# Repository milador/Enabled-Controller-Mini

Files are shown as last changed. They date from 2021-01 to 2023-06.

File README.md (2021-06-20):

# Enabled-Controller-Mini

Enabled Controller Mini is a more affordable version of <a href="https://github.com/milador/Enabled-Controller">Enabled-Controller</a> which is an open-source switch controller interface that enables those with limited or no hand movement to use Adaptive switches as input to operate and perform joystick actions.

<p align="center">
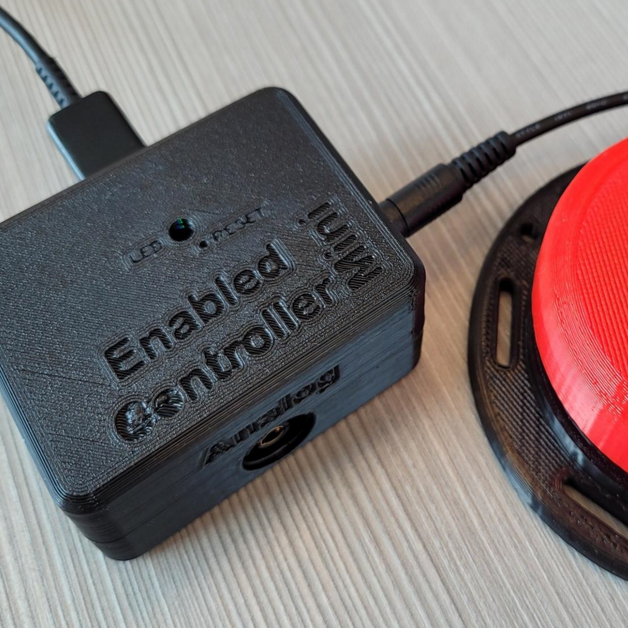
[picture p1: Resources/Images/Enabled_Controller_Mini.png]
Enabled Controller Mini

</p>

The device offers up to four switch input enclosures through four 3.5mm audio jacks and two analog inputs through one 3.5mm headphone jack. The one 3.5mm headphone jacks can be used to connect one X-Y analog joystick.

The internal RGB led of QT Py board is used to provide visual feedback for each action.

## Assembly Instructions Manual

The <a href="https://github.com/milador/Enabled-Controller-Mini/blob/main/Documentation/Build_Manuals/Enabled_Controller_Mini_Instructions_Manual.pdf">Assembly Instructions Manual</a> is available to download.

## Parts

The <a href="https://github.com/milador/Enabled-Controller-Mini/blob/main/Components/Enabled_Controller_Mini_BOM.csv">BOM</a> file is available to download.

## Software

The first experimental software is under testing.

## Hardware 

### PCB Design 

The <a href="https://github.com/milador/Enabled-Controller-Mini/tree/main/Hardware/PCB">PCB files</a> including both PCB Eagle design files and generated gerber files are available to download.

### Enclosure

The <a href="https://github.com/milador/Enabled-Controller-Mini/tree/main/Hardware/Enclosure">Enclosure files</a> including both STL and STEP enclosure files are available to download.

## License

### Creative Commons Attribution-NonCommercial-ShareAlike (CC-BY-NC-SA)

Copyright (c) 2021 Milador

A creative commons license that bans commercial use and requires you to release any modified works under this license.

<p align="center">
CC-BY-NC-SA
</p>

<br />This work is licensed under a <a rel="license" href="http://creativecommons.org/licenses/by-nc-sa/3.0/">Creative Commons Attribution-NonCommercial-ShareAlike 3.0 Unported License</a>.

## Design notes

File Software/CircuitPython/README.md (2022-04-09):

# Enabled-Controller-Mini CircuitPython software setup

  1. Download the latest version of [CircuitPython for QT Py UF2](https://circuitpython.org/board/qtpy_m0/) from official website or the latest [Tested CircuitPython for QT Py UF2](https://github.com/milador/Enabled-Controller-Mini/raw/main/Software/CircuitPython/UF2/adafruit-circuitpython-qtpy_m0-en_US-6.0.1.uf2) from this repository.
  2. Plug your QT Py into your computer using a known-good USB cable
  3. Double-click the small RST (reset) button, and you will see the NeoPixel RGB LED turn green
  4. You will see a new disk drive appear called QTPY_BOOT under Device and Drivers 
  5. Drag the adafruit_circuitpython_etc.uf2 file to QTPY_BOOT
  6. The red LED will flash. Then, the QTPY_BOOT drive will disappear and a new disk drive called CIRCUITPY will appear
  7. Replace the code.py under CIRCUITPY drive with Enabled-Controller-Mini USB [code.py](https://raw.githubusercontent.com/milador/Enabled-Controller-Mini/main/Software/CircuitPython/Enabled_Controller_Mini_USB_Software/code.py)
  8. Drag and drop required libraries under CIRCUITPY drive in lib folder. [Required libraries](https://github.com/milador/Enabled-Controller-Mini/tree/main/Software/CircuitPython/Enabled_Controller_Mini_USB_Software/lib)
  9. The led on Enabled-Controller-Mini should turn to teal color

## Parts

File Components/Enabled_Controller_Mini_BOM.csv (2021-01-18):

Index | Quantity | Digikey Part Number | Manufacturer Part Number | Description | Price (CAD) | Unit Price (CAD) | Link
1 | 1 | 1528-4600-ND | 4600 | ADAFRUIT QT PY - SAMD21 DEV BOARD | 8.31 | 8.31 | https://www.digikey.ca/en/products/detail/adafruit-industries-llc/4600/13543375
2 | 2 | S7040-ND | PPPC071LFBN-RC | CONN HDR 7POS 0.1 GOLD | 0.84 | 0.84 | https://www.digikey.ca/en/products/detail/sullins-connector-solutions/PPPC071LFBN-RC/810179
3 | 4 | CP1-3535NG-ND | SJ1-3535NG | CONN JACK STEREO 3.5MM R/A | 1.65 | 1.65 | https://www.digikey.ca/product-detail/en/cui-inc/SJ1-3535NG/CP1-3535NG-ND
4 | 1 | CP-43514-ND | SJ-43514 | CONN JACK 4COND 3.5MM | 1.47 | 1.47 | https://www.digikey.ca/en/products/detail/SJ-43514/CP-43514-ND/368146
5 | 4 | 36-4701-ND | 4701 | HEX NUT 0.245" STEEL 6-32 | 0.15 | 0.15 | https://www.digikey.ca/en/products/detail/keystone-electronics/4701/316272
6 | 4 | 36-9309-ND | 9309 | MACH SCREW PAN HEAD SLOTTED 6-32 | 0.15 | 0.15 | https://www.digikey.ca/en/products/detail/keystone-electronics/9309/2746088
 |  |  |  |  | Total Price (CAD) | 19.26

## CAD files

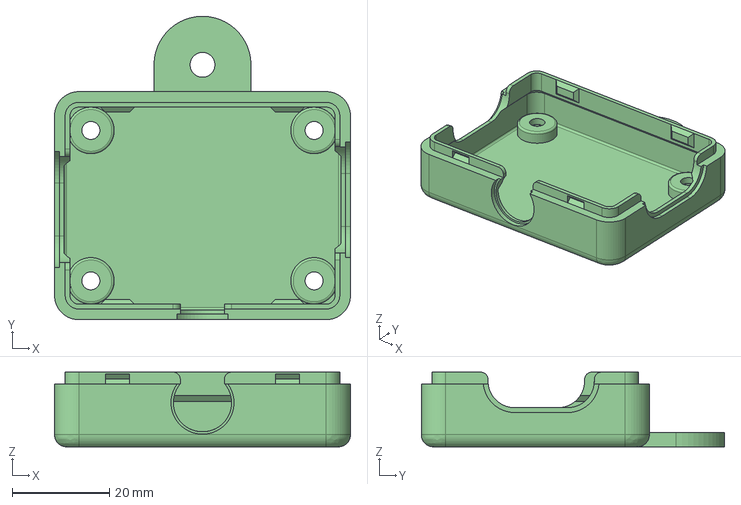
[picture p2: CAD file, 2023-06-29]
Hardware/Enclosure/STEP/Enabled_Controller_Mini_Bottom_With_Mount.step
61.0 x 62.5 x 15.4 mm

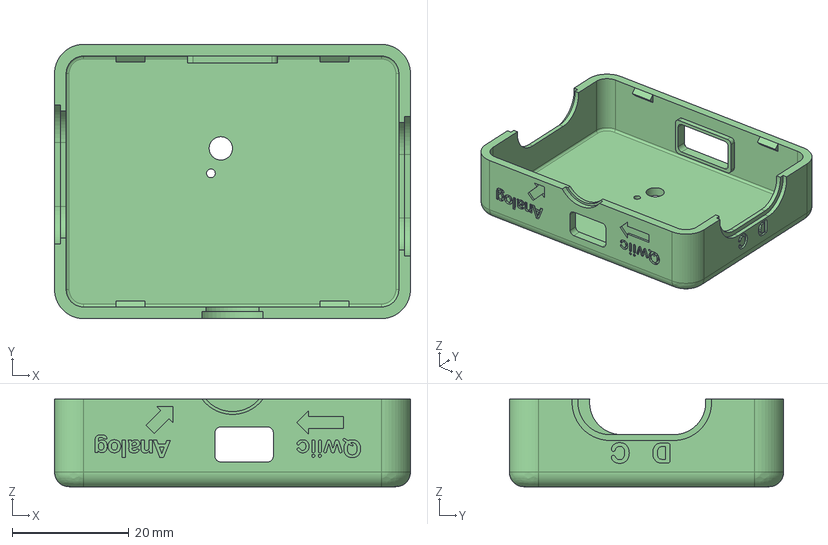
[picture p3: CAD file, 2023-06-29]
Hardware/Enclosure/STEP/Enabled_Controller_Mini_Top.step
61.0 x 47.0 x 15.0 mm

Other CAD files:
Hardware/Enclosure/STEP/Enabled_Controller_Mini_Bottom.step
Hardware/Enclosure/STL/Enabled_Controller_Mini_Bottom.stl
Hardware/Enclosure/STL/Enabled_Controller_Mini_Bottom_With_Mount.stl
Hardware/Enclosure/STL/Enabled_Controller_Mini_Top.stl

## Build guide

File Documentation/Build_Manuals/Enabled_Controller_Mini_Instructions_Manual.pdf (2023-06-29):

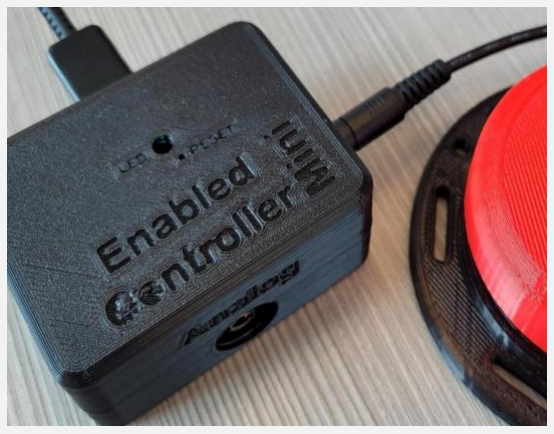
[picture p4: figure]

# ENABLED-CONTROLLER-MINI INSTRUCTIONS MANUAL (V1.3)

An accessible switch adapter box for gaming

### Milad Hajihassan

https://github.com/milador/Enabled-Controller-Mini

1

## Contents

Components List | 2
Software | 3
Installing Arduino IDE | 3
Installing Arduino Libraries | 3
USB Version | 3
Board Support Packages | 3
Required Software and libraries | 4
Uploading Software | 5
Joystick Version | 6
Board Support Packages | 6
Required Software and libraries | 6
Uploading Software | 7
Hardware Assembly | 8
Printed circuit Board design | 8
Enclosure design | 8
Enabled-Controller-Mini Assembly | 9
Joystick Assembly | 21

2

## Components List

1. ADAFRUIT QT PY - SAMD21 DEV BOARD x 1
2. 7 POSITION HEADER x 2
3. CONN JACK STEREO 3.5MM R/A x 4
4. CONN JACK 4COND 3.5MM x 1
5. ANALOG 2-AXIS THUMB JOYSTICK WIT (Optional) x 1
6. HEX NUT 0.245" STEEL 6-32 x 4
7. MACH SCREW PAN HEAD SLOTTED 6-32 x 4

The bill of materials can also be downloaded from GitHub repository under main directory.

https://github.com/milador/Enabled-Controller-

Mini/blob/master/Components/Enabled_Controller_Mini_BOM.csv (https://github.com/milador/Enabled-Controller-Mini/blob/master/Components/Enabled_Controller_Mini_BOM.csv)

3

## Software

The Enabled-Controller-Mini software can be downloaded from the GitHub repository under software directory.

https://github.com/milador/Enabled-Controller-Mini/tree/master/Software/Arduino/

There are two flavors of Enabled-Controller-Mini and each one requires different hardware. The Enabled-Controller-Mini software is offered in the following flavors:

1. USB Keyboard/Mouse Version
2. Joystick Version

### Installing Arduino IDE

The Arduino IDE is required to compile and upload the source code to the MCU in your Adafruit QT Py board. You can download and install the Arduino from official Arduino website that you can find using following link:

https://www.arduino.cc/en/software

### Installing Arduino Libraries

The following instructions on how to install additional Arduino libraries helps you to get started with setting up Arduino IDE with required libraries and dependencies.

https://www.arduino.cc/en/guide/libraries

### USB Version

Board Support Packages
You can find the official instructions to install Board Support Packages on Adafruit website using following link:

https://learn.adafruit.com/adafruit-qt-py/arduino-ide-setup

Alternatively, you can perform following instructions to install Board Support Packages:

1. Open and start the Arduino IDE.
2. Go to File > Preferences.
3. Add following link as a new line under Additional Board Manager URLs
- https://adafruit.github.io/arduino-board-index/package_adafruit_index.json
4. Restart the Arduino IDE
5. Open the Boards Manager option from the Tools > Board menu and install Adafruit SAMD Boards by Adafruit
6. Wait until the IDE finishes installing the cross-compiling toolchain and tools associated with Board Support Package. This may take few minutes.
7. That’s it! The installation of Board Support Packages is finished.

4

Required Software and libraries
The USB version of the software requires the following files and libraries:
- StopWatch library (https://github.com/RobTillaart/Stopwatch_RT)
- EasyMorse library (https://github.com/milador/EasyMorse)
- Adafruit_NeoPixel library (https://github.com/adafruit/Adafruit_NeoPixel)
- FlashStorage library (https://github.com/cmaglie/FlashStorage)
- Enabled_Controller_Mini_USB_Software.ino (https://raw.githubusercontent.com/milador/Enabled-Controller-Mini/main/Software/Arduino/Enabled_Controller_Mini_USB_Software/Enabled_Controller_Mini_USB_Softw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)

StopWatch library helps to calculate the reaction time and timeout in the morse code interface.

Enabled-Controller-Mini is using Adafruit_NeoPixel library to provide visual feedback using RGB LED.

You can use the following instructions to download and install the required libraries:

1) Visit the StopWatch library (https://github.com/RobTillaart/Stopwatch_RT) github repository page.
2) Click on Code > Download Zip to download StopWatch library.
3) Extract Stopwatch_RT-master.zip file
4) Rename Stopwatch_RT-master folder to Stopwatch folder under Stopwatch_RT-master subdirectory.
5) Copy or move Stopwatch folder to Arduino installation library subdirectory. As an example: This is found under C:\Program Files (x86)\Arduino\libraries in windows 10.
6) Visit the EasyMorse library (https://github.com/milador/EasyMorse) github repository page.
7) Click on Code > Download Zip to download EasyMorse library.
8) Extract EasyMorse-master.zip file
9) Rename EasyMorse-master folder to EasyMorse folder under EasyMorse-master subdirectory.
10) Copy or move EasyMorse folder to Arduino installation library subdirectory. As an example: This is found under C:\Program Files (x86)\Arduino\libraries in windows 10.
11) Visit the FlashStorage library (https://github.com/cmaglie/FlashStorage) github repository page.
12) Click on Code > Download Zip to download FlashStorage library.
13) Extract FlashStorage-master.zip file
14) Rename FlashStorage-master folder to FlashStorage folder under FlashStorage-master subdirectory.
15) Copy or move FlashStorage folder to Arduino installation library subdirectory. As an example: This is found under C:\Program Files (x86)\Arduino\libraries in windows 10.
16) Visit the Enabled_Controller_Mini_USB_Software.ino (https://raw.githubusercontent.com/milador/Enabled-Controller-Mini/main/Software/Arduino/Enabled_Controller_Mini_USB_Software/Enabled_Controller_Mini_USB_Softw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) raw source code file under Enabled-Controller-Mini github repository page.
17) Right click on the source code or any place on this page and select Save Page As…
18) Select the directory you would like to save the software in your computer.
19) Change File name from Enabled_Controller_Mini_USB_Software to Enabled_Controller_Mini_USB_Software.ino
20) Change Save as type to All Files.
21) Click on Save button.
22) Open the directory you selected in step 18.
23) Double left click or open Enabled_Controller_Mini_USB_Software file

5

24) Arduino IDE will ask your permission to create a new sketch folder named Enabled_Controller_Mini_USB_Software and move Enabled_Controller_Mini_USB_Software.ino under this folder.
25) Click on the Ok button.
26) Arduino IDE should now open the Enabled_Controller_Mini_USB_Software.ino file automatically.

Uploading Software
Note: Make sure all files are included in your local copy of Software directory before uploading it to the Adafruit QT PY board. The libraries can be installed in Arduino libraries.

You can go ahead and upload the downloaded .ino code to Adafruit QT PY board using Arduino IDE once all the necessary libraries are installed.

1. Start the Arduino IDE
2. Open Enabled_Controller_Mini_USB_Software.ino
3. Select the Board under Tools > Board > Adafruit SAMD Boards as Adafruit QT PY (SAMD21)
4. Select the correct port number under Tools > Port which should show COM XX (Adafruit QT PY)

Note: It’s very important to make sure the correct Board and port number are selected as selecting the wrong board may result problems with bootloader of Adafruit QT PY board.

5. Press the Verify button to make sure there is no problem with the software and libraries.
6. Press Upload button

You can now go ahead and upload the software. Arduino IDE will show you a Done Uploading message indicating the software is uploaded to your Enabled-Controller-Mini.

The LED on the QT PY board blinks two times in teal to indicate the start of initialization process has been started and it will blink again two times in green to indicate end of the initialization process.

You can also open the Serial Monitor in Arduino IDE on 115200 baud-rate to read initialization information about the version of software.

6

### Joystick Version

Board Support Packages
You can find the official instructions to install Board Support Packages on Adafruit website using following link:

https://learn.adafruit.com/adafruit-qt-py/arduino-ide-setup

Alternatively, you can perform following instructions to install Board Support Packages:

1. Open and start the Arduino IDE.
2. Go to File > Preferences.
3. Add following link as a new line under Additional Board Manager URLs
- https://adafruit.github.io/arduino-board-index/package_adafruit_index.json
4. Restart the Arduino IDE
5. Open the Boards Manager option from the Tools > Board menu and install Adafruit SAMD Boards by Adafruit
6. Wait until the IDE finishes installing the cross-compiling toolchain and tools associated with Board Support Package. This may take few minutes.
7. That’s it! The installation of Board Support Packages is finished.

Required Software and libraries
The Joystick version of the software requires the following files and libraries:
- XACGamepad.h header file (https://github.com/milador/Enabled-Controller-Mini/tree/main/Software/Arduino/Enabled_Controller_Mini_Joystick_Software/XACGamepad.h)
- Adafruit_NeoPixel library (https://github.com/adafruit/Adafruit_NeoPixel)
- Enabled_Controller_Mini_Joystick_Software.ino (https://raw.githubusercontent.com/milador/Enabled-Controller-Mini/main/Software/Arduino/Enabled_Controller_Mini_Joystick_Software/Enabled_Controller_Mini_Joys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)

The XACGamepad.h header file (https://github.com/milador/Enabled-Controller-Mini/tree/main/Software/Arduino/Enabled_Controller_Mini_Joystick_Software/XACGamepad.h) is used to turn Enabled Controller Mini into a XAC Compatible joystick USB HID device which can be used for gaming. It uses TinyUSB USB stack instead of Arduino USB stack to create custom Gamepad USB descriptor.

Enabled-Controller-Mini is using Adafruit_NeoPixel library to provide visual feedback using RGB LED.

You can use the following instructions to download and install the required libraries:

1) Visit the Enabled_Controller_Joystick_Software.ino (https://raw.githubusercontent.com/milador/Enabled-Controller-Mini/main/Software/Arduino/Enabled_Controller_Mini_Joystick_Software/Enabled_Controller_Mini_Joys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) raw source code file under Enabled-Controller-Mini github repository page.
2) Right click on the source code or any place on this page and select Save Page As…
3) Select the directory you would like to save the software in your computer.
4) Change File name from Enabled_Controller_Mini_Joystick_Software to Enabled_Controller_Mini_Joystick_Software.ino
5) Change Save as type to All Files.
6) Click on Save button.
7) Visit the XACGamepad.h header file (https://github.com/milador/Enabled-Controller-Mini/tree/main/Software/Arduino/Enabled_Controller_Mini_Joystick_Software/XACGamepad.h) raw source code file under Enabled-Controller-Mini github repository page.
8) Right click on the source code or any place on this page and select Save Page As…

7

9) Select the same directory that you previously saved Enabled_Controller_Mini_Joystick_Software.ino in step 4.
10) Change File name from XACGamepad to XACGamepad.h
11) Change Save as type to All Files.
12) Click on the Save button.
13) Open the directory you selected in step 4.
14) Double left click or open Enabled_Controller_Mini_Joystick_Software file
15) Arduino IDE will ask your permission to create a new sketch folder named Enabled_Controller_Mini_Joystick_Software and move Enabled_Controller_Mini_Joystick_Software.ino under this folder.
16) Click on the Ok button.
17) Arduino IDE should now open the Enabled_Controller_Mini_Joystick_Software.ino file automatically.

Uploading Software
Note: Make sure all files are included in your local copy of Software directory before uploading it to the Adafruit QT PY board. The libraries can be installed in Arduino libraries.

You can go ahead and upload the downloaded .ino code to Adafruit QT Py board using Arduino IDE once all the necessary libraries are installed.

1. Start the Arduino IDE
2. Open Enabled_Controller_Mini_Joystick _Software.ino
3. Select the Board under Tools > Board > Adafruit SAMD Boards as Adafruit QT PY (SAMD21)
4. Select the USB Stack Tools > USB Stack as TinyUSB
5. Select the correct port number under Tools > Port which should show COM XX (Adafruit QT PY)

Note: It’s very important to make sure the correct Board and port number are selected as selecting the wrong board may result problems with bootloader of Adafruit QT PY board.

6. Press the Verify button to make sure there is no problem with the software and libraries.
7. Press Upload button

You can now go ahead and upload the software. Arduino IDE will show you a Done Uploading message indicating the software is uploaded to your Enabled-Controller-Mini.

The LED on the QT PY board blinks two times in teal to indicate the start of initialization process has been started and it will blink again two times in green to indicate end of the initialization process.

You can also open the Serial Monitor in Arduino IDE on 115200 baud-rate to read initialization information about the version of software.

8

## Hardware Assembly

### Printed circuit Board design

The printed circuit boards (PCB) can be downloaded from GitHub repository under Hardware directory.

https://github.com/milador/Enabled-Controller-Mini/tree/master/Hardware/PCB

### Enclosure design

The enclosure/housing files in STL format can be downloaded from GitHub repository under Hardware directory.

https://github.com/milador/Enabled-Controller-Mini/tree/master/Hardware/Enclosure

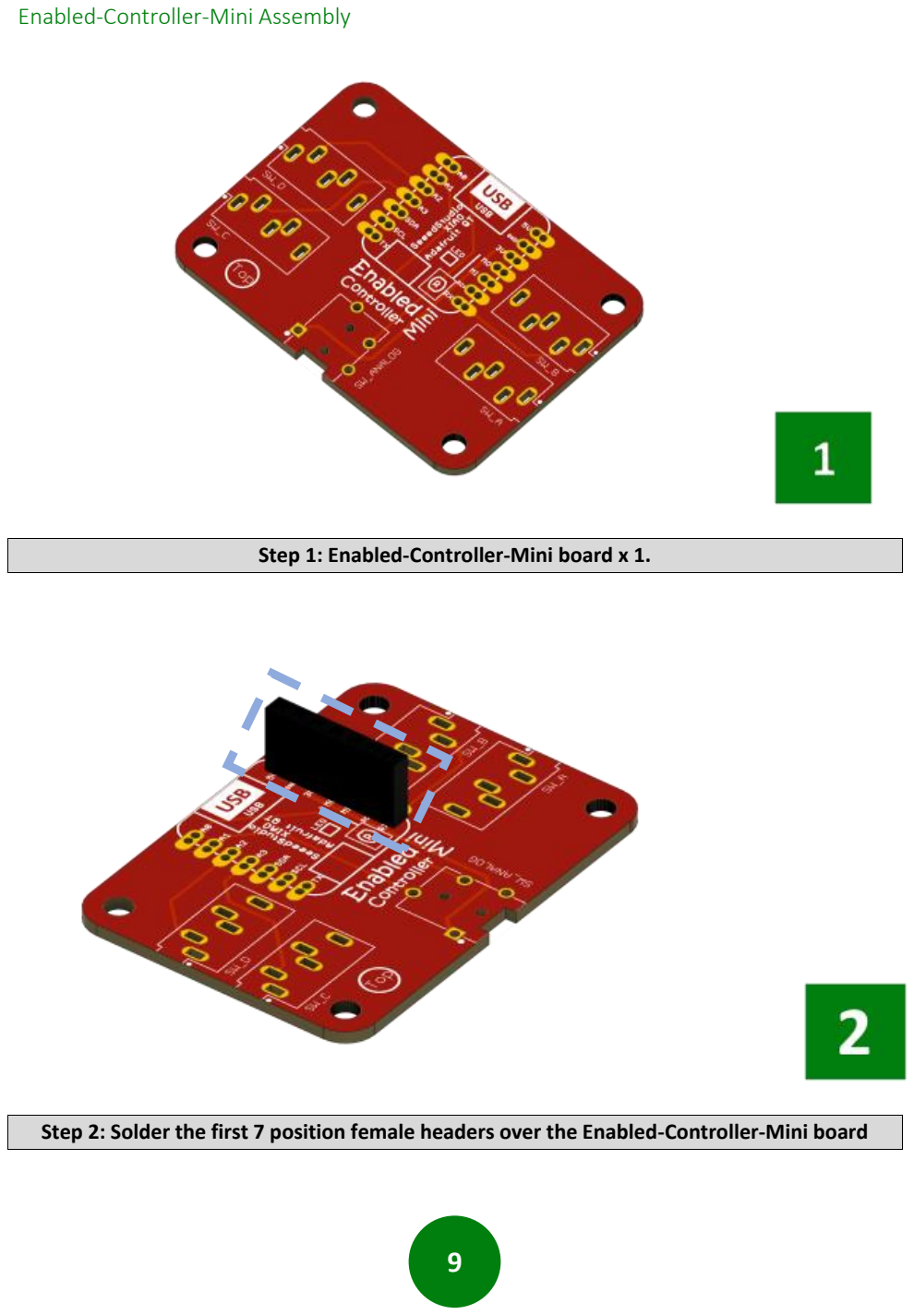
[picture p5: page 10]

9

### Enabled-Controller-Mini Assembly

Step 1: Enabled-Controller-Mini board x 1.
Step 2: Solder the first 7 position female headers over the Enabled-Controller-Mini board

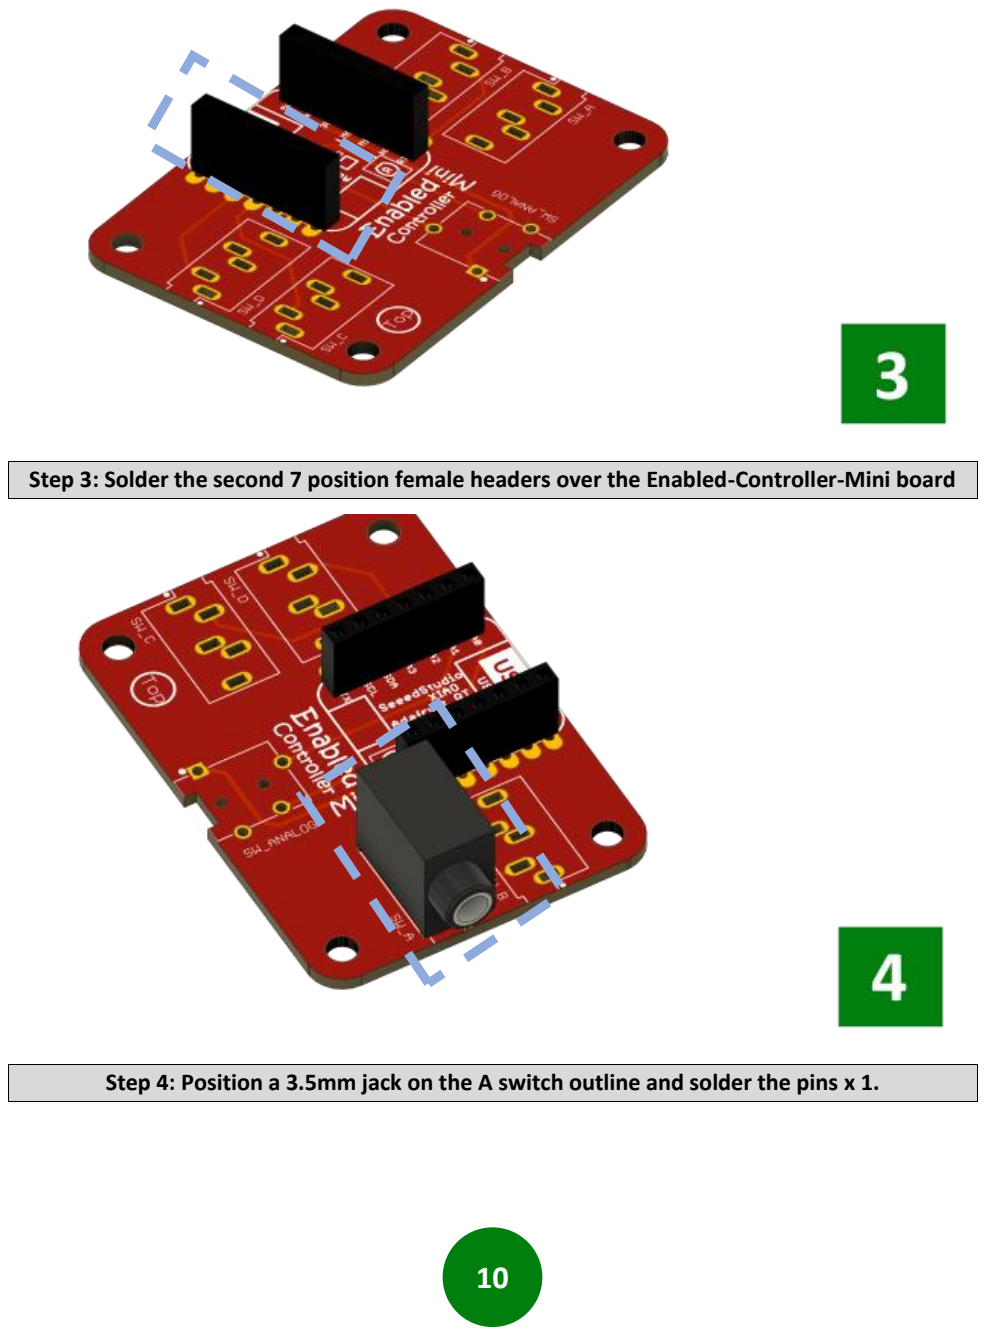
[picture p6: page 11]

10

Step 3: Solder the second 7 position female headers over the Enabled-Controller-Mini board
Step 4: Position a 3.5mm jack on the A switch outline and solder the pins x 1.

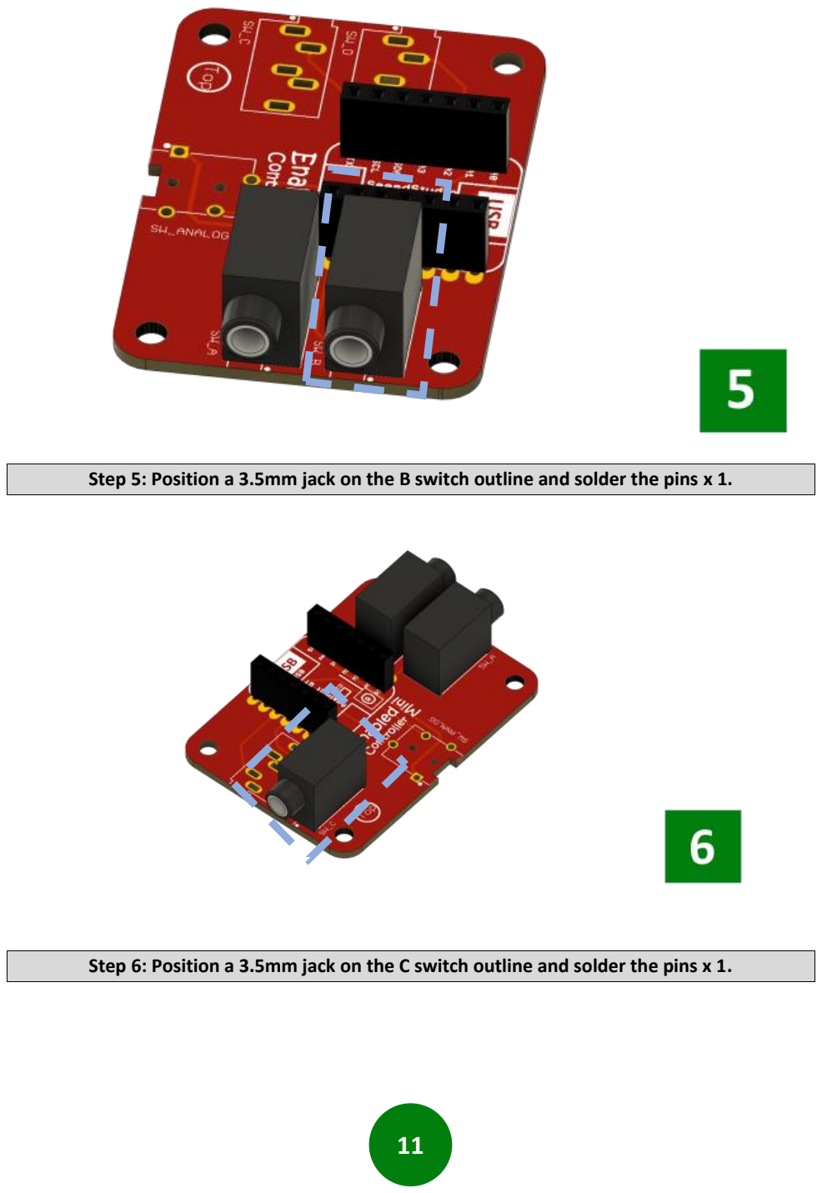
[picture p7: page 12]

11

Step 5: Position a 3.5mm jack on the B switch outline and solder the pins x 1.
Step 6: Position a 3.5mm jack on the C switch outline and solder the pins x 1.

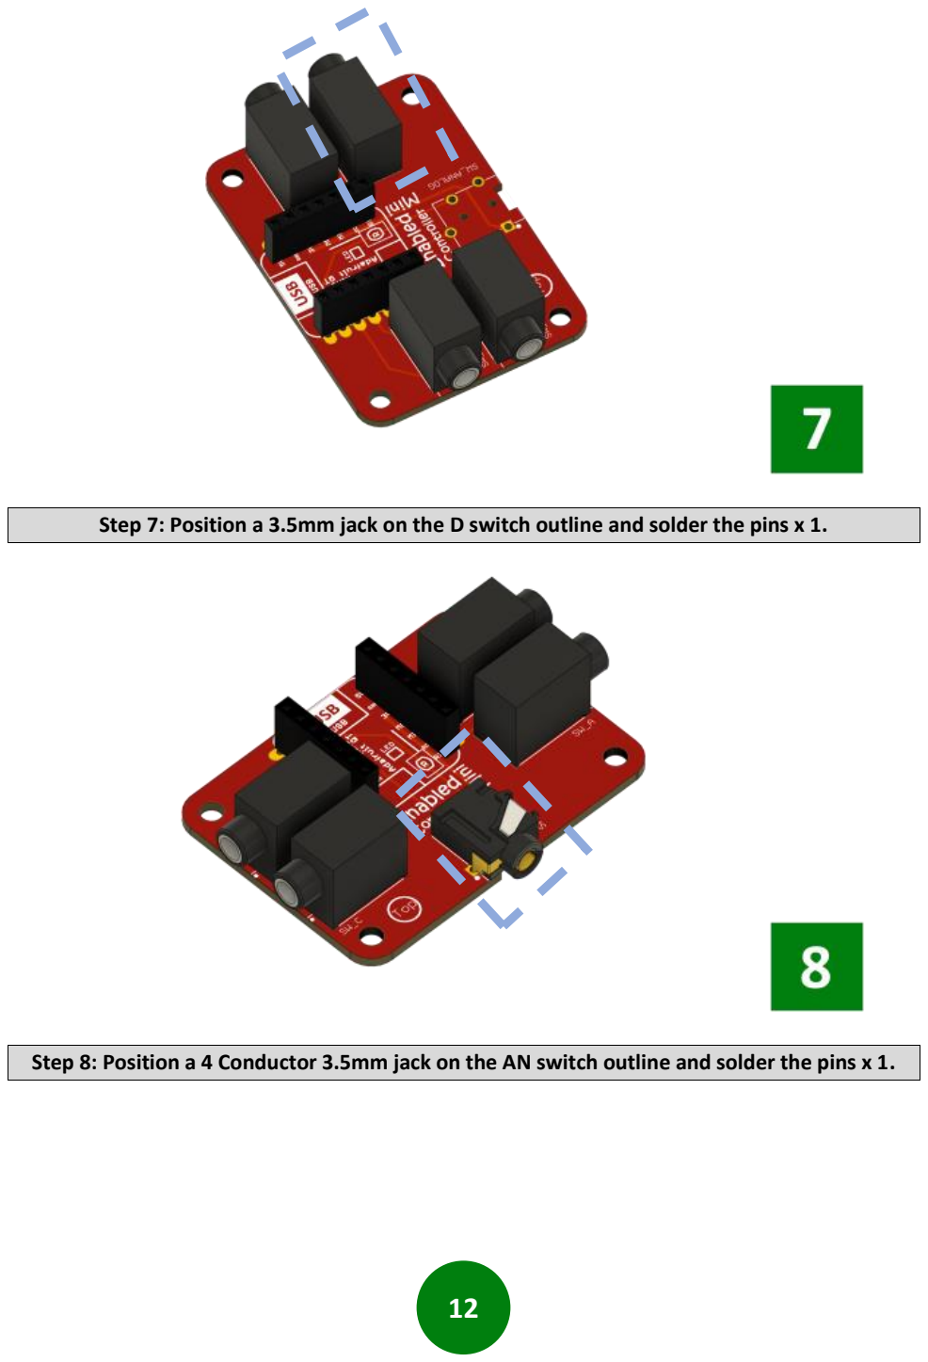
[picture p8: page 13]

12

Step 7: Position a 3.5mm jack on the D switch outline and solder the pins x 1.
Step 8: Position a 4 Conductor 3.5mm jack on the AN switch outline and solder the pins x 1.

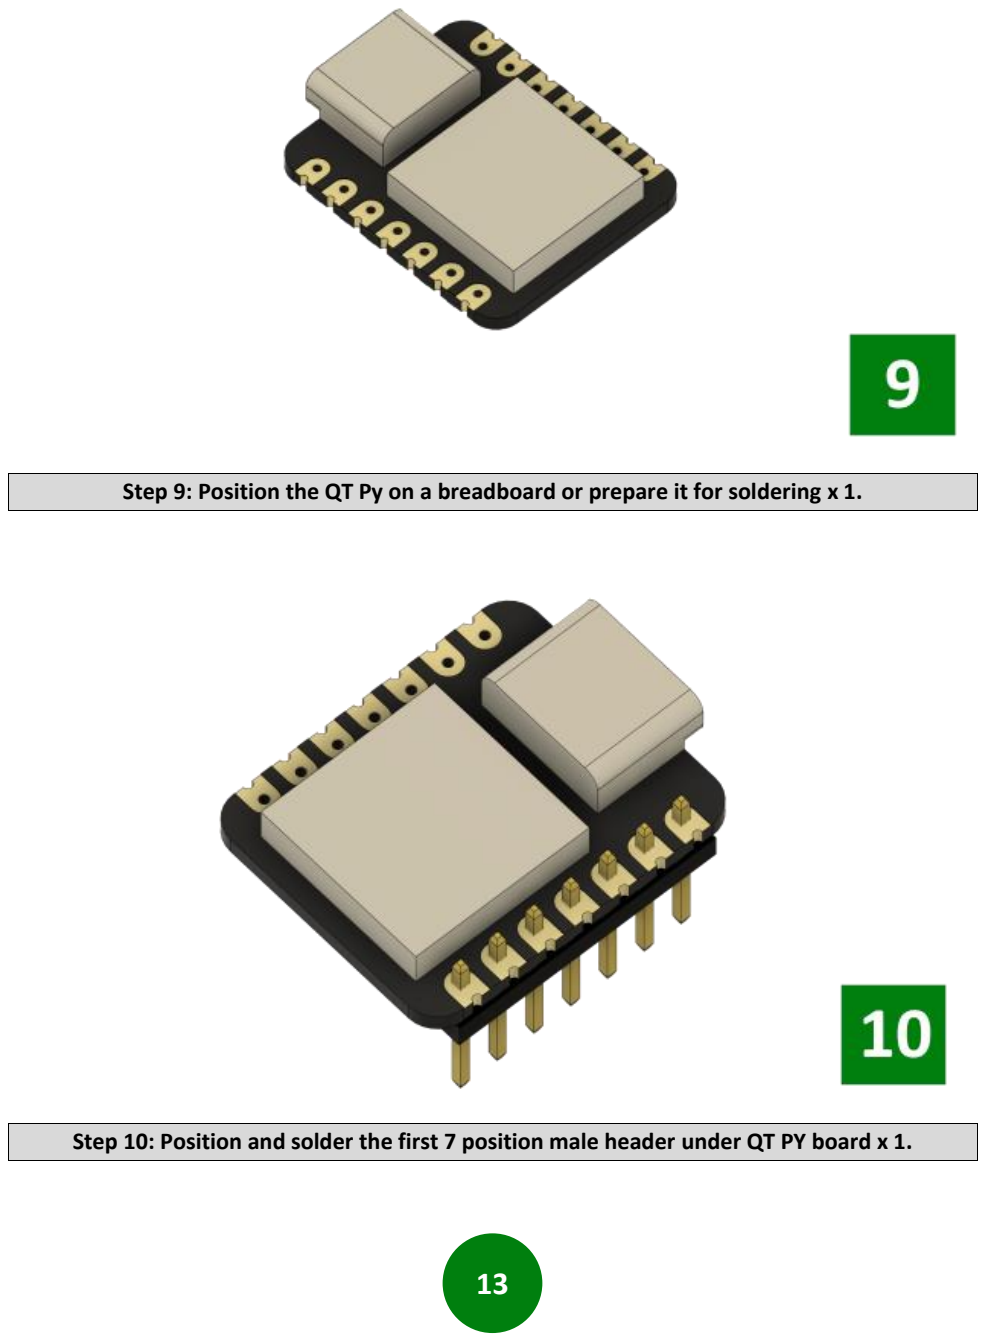
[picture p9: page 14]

13

Step 9: Position the QT Py on a breadboard or prepare it for soldering x 1.
Step 10: Position and solder the first 7 position male header under QT PY board x 1.

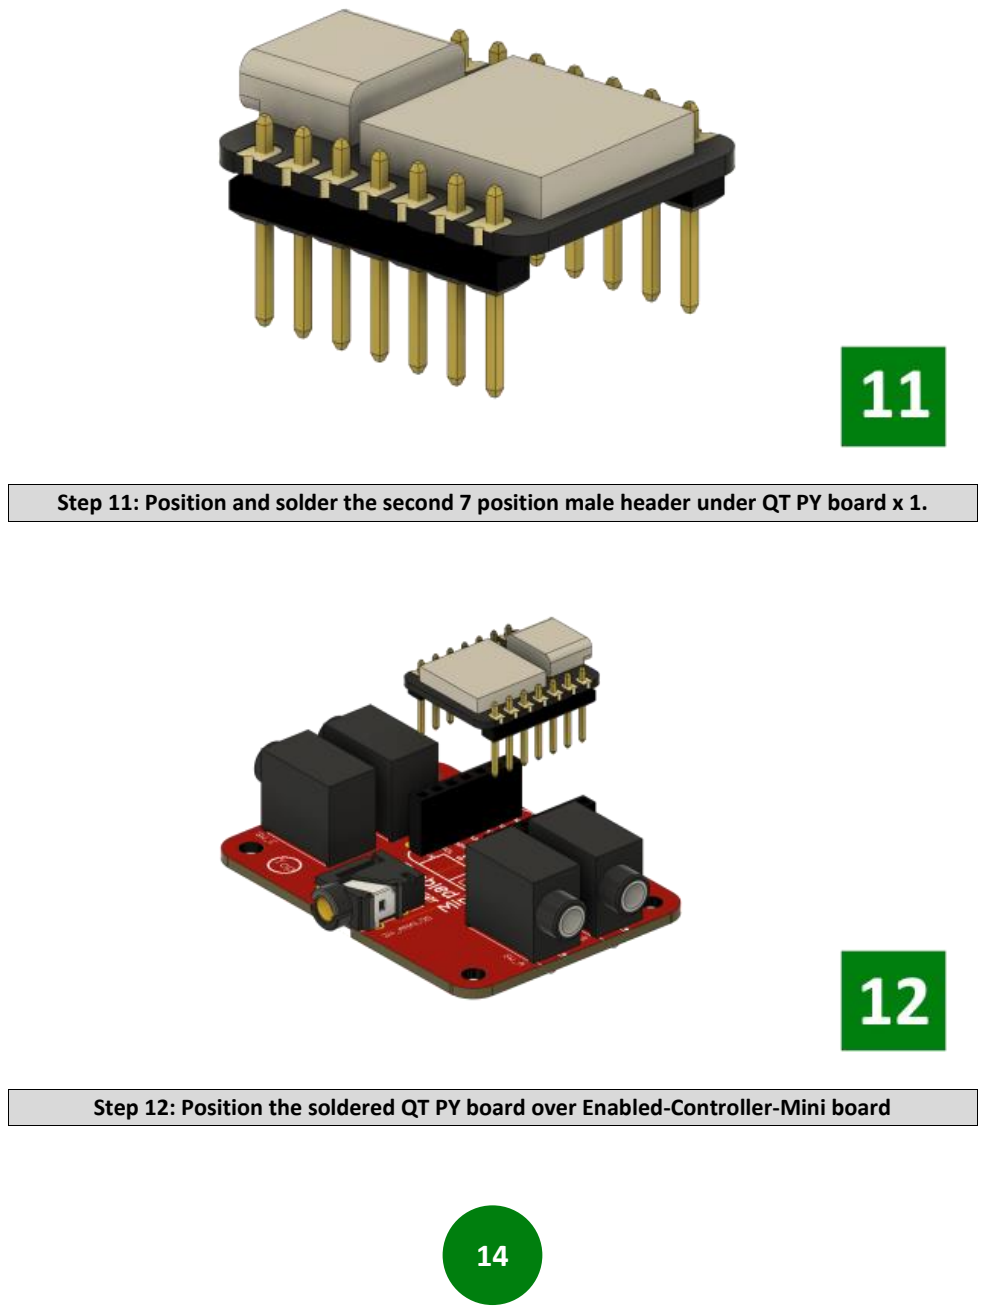
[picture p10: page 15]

14

Step 11: Position and solder the second 7 position male header under QT PY board x 1.
Step 12: Position the soldered QT PY board over Enabled-Controller-Mini board

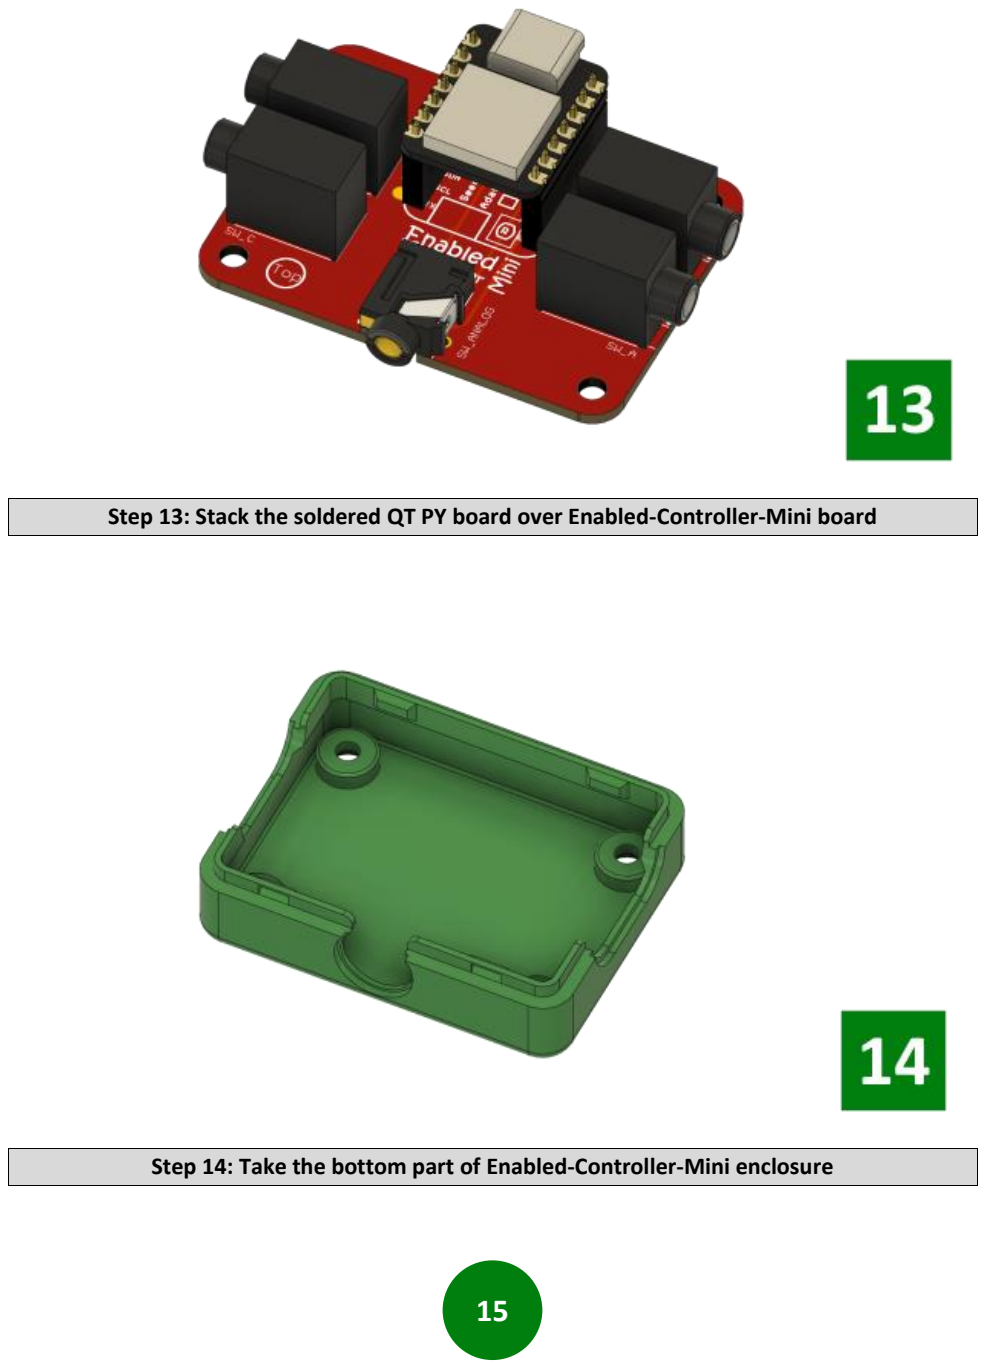
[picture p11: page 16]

15

Step 13: Stack the soldered QT PY board over Enabled-Controller-Mini board
Step 14: Take the bottom part of Enabled-Controller-Mini enclosure

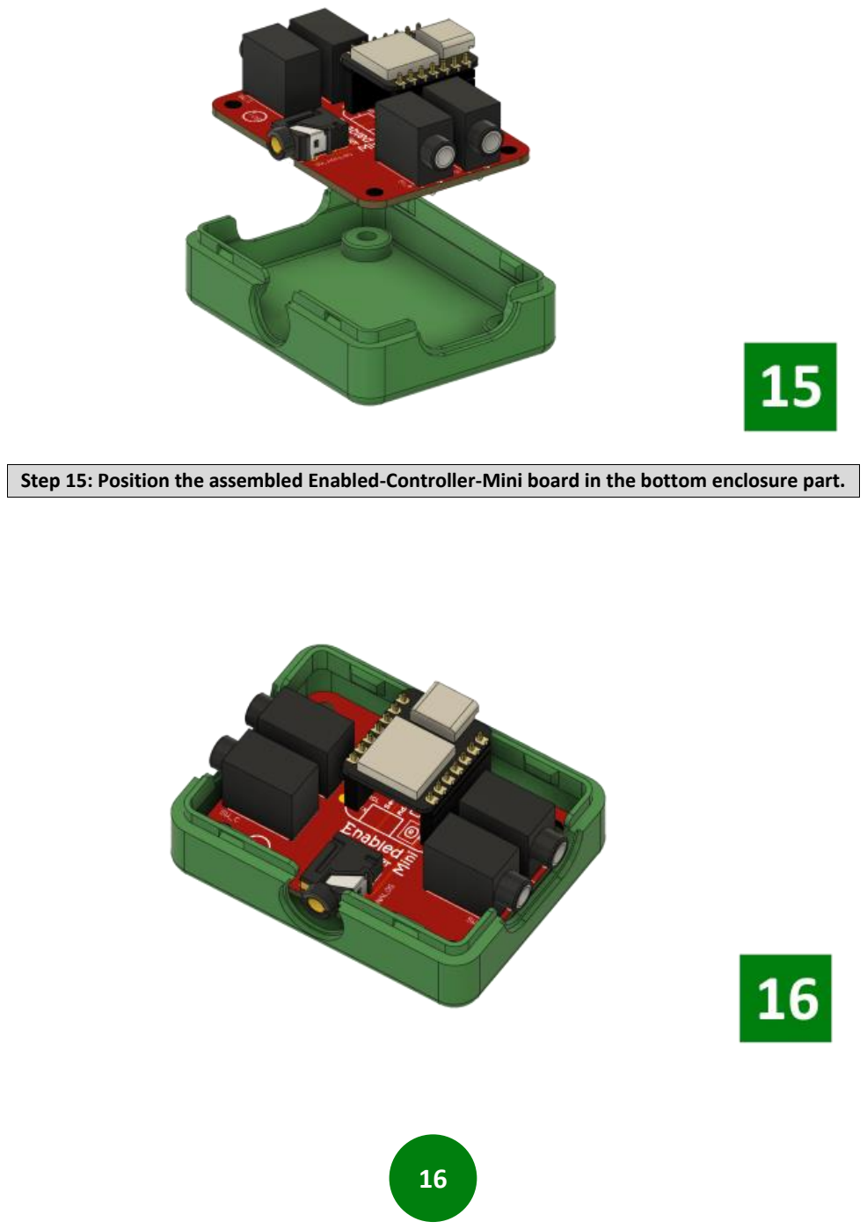
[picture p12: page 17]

16

Step 15: Position the assembled Enabled-Controller-Mini board in the bottom enclosure part.

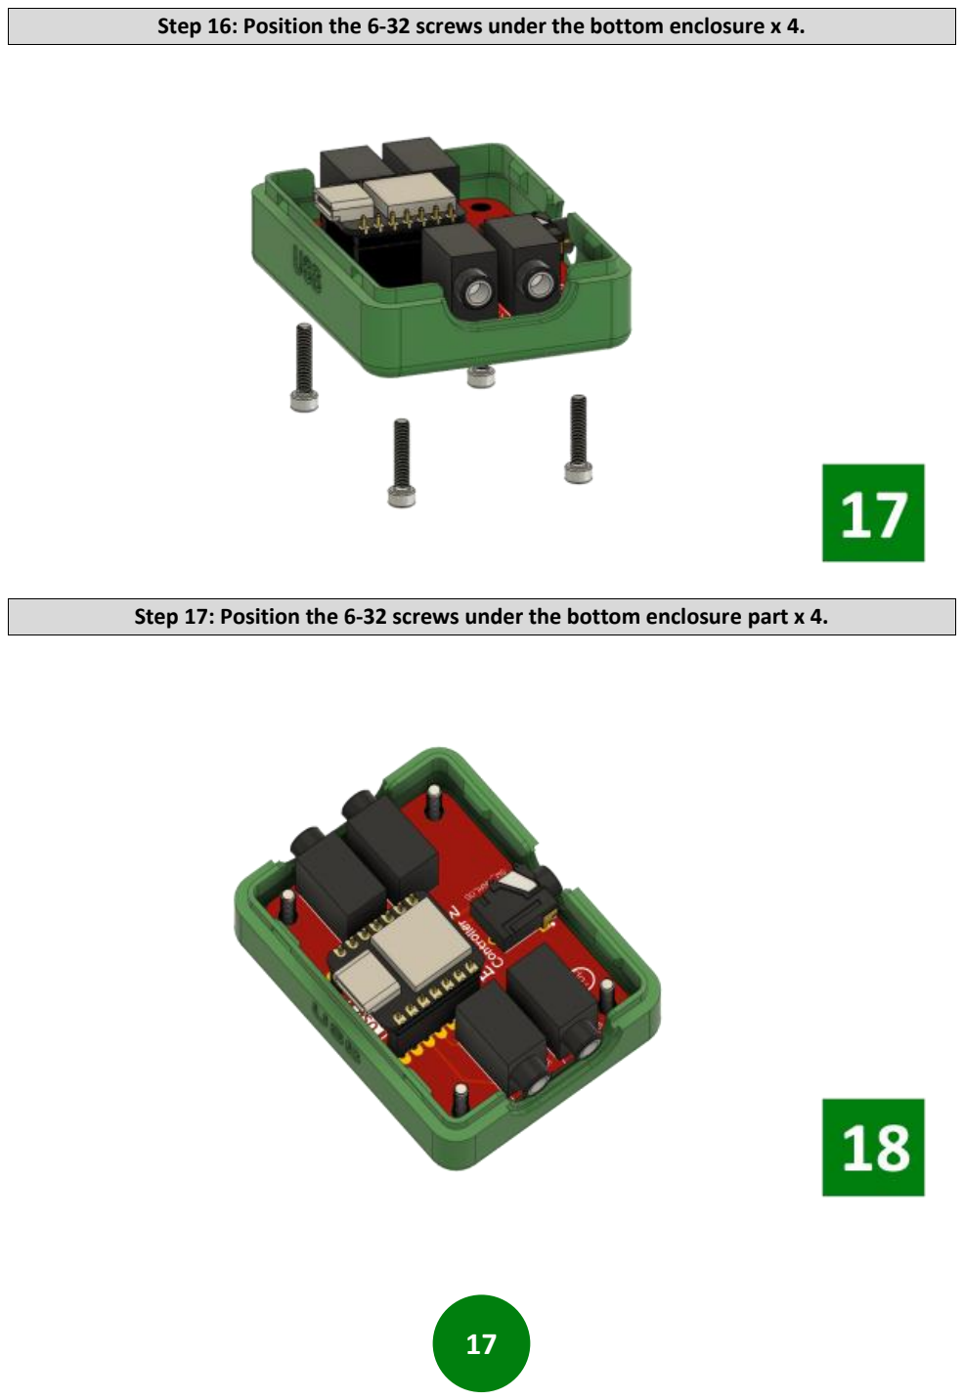
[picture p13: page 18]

17

Step 16: Position the 6-32 screws under the bottom enclosure x 4.
Step 17: Position the 6-32 screws under the bottom enclosure part x 4.

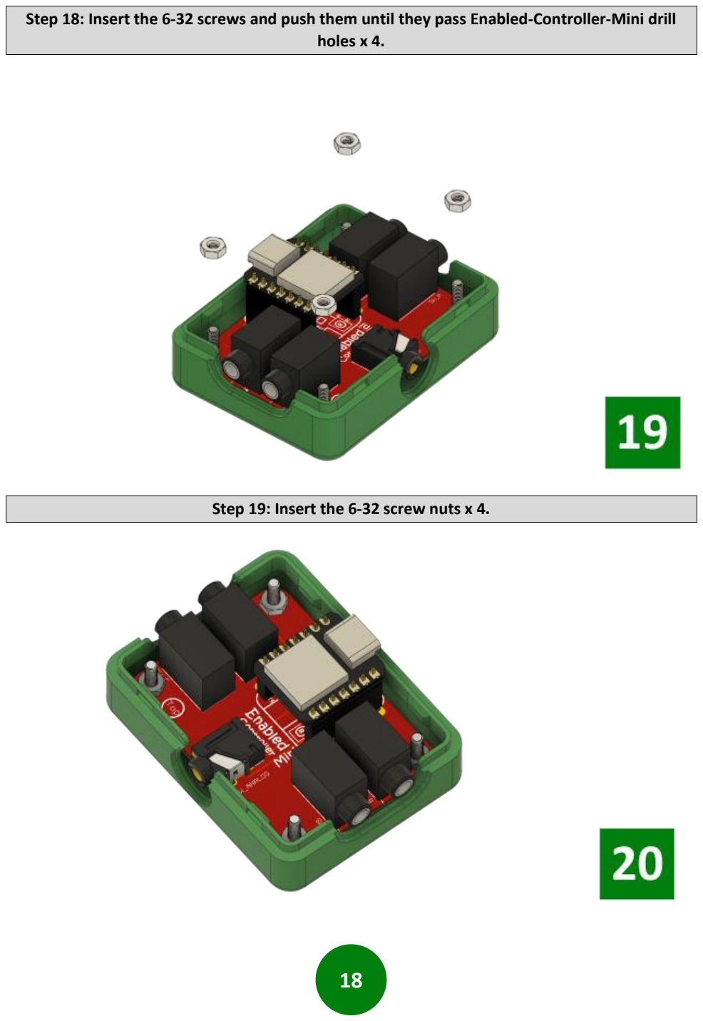
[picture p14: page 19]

18

Step 18: Insert the 6-32 screws and push them until they pass Enabled-Controller-Mini drill holes x 4.
Step 19: Insert the 6-32 screw nuts x 4.

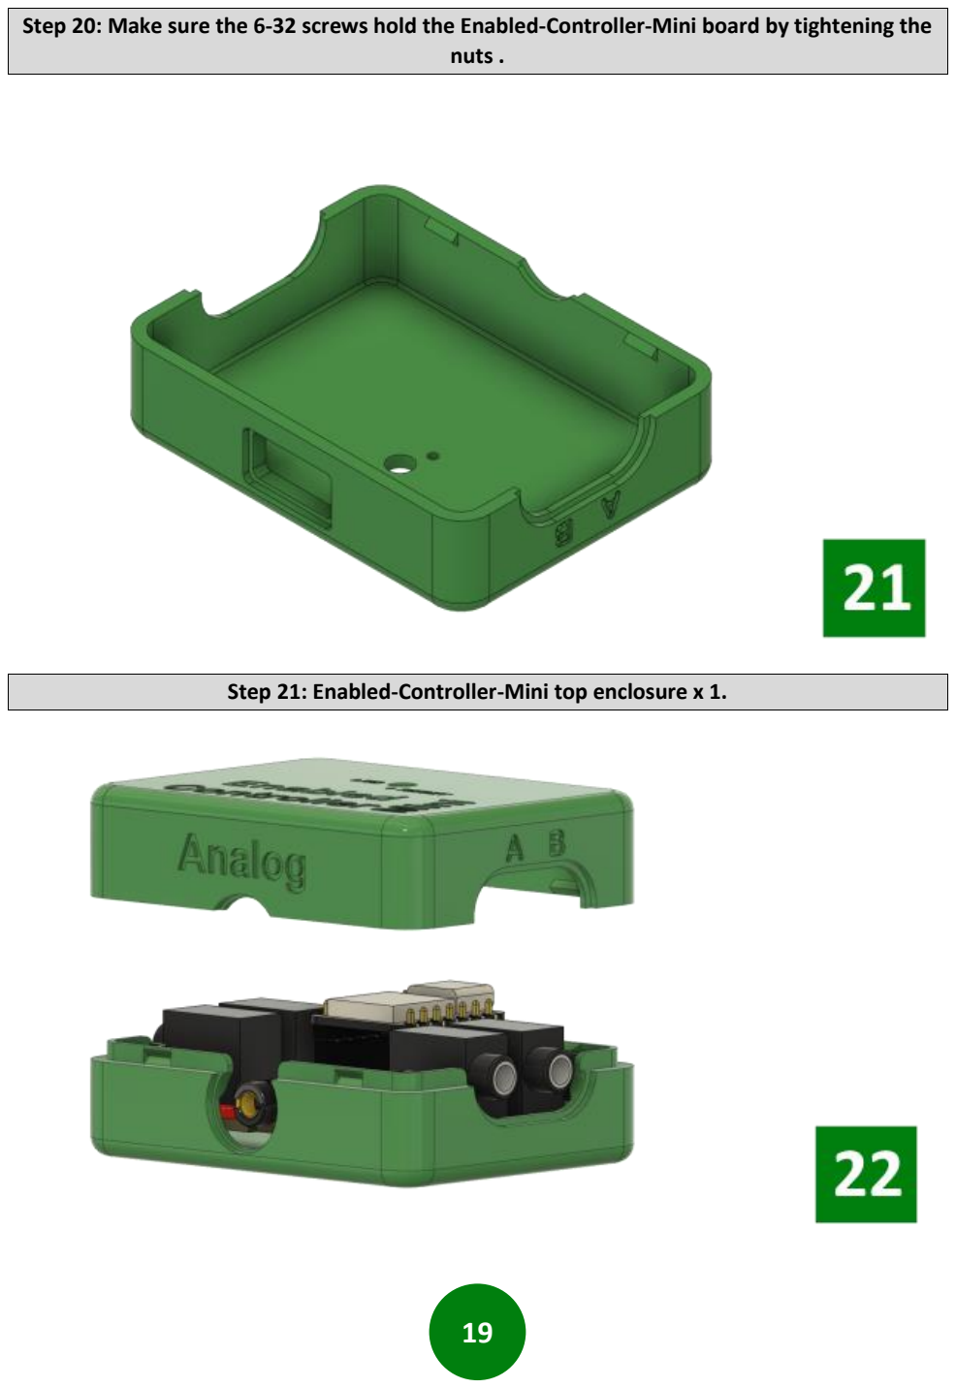
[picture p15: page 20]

19

Step 20: Make sure the 6-32 screws hold the Enabled-Controller-Mini board by tightening the nuts .
Step 21: Enabled-Controller-Mini top enclosure x 1.

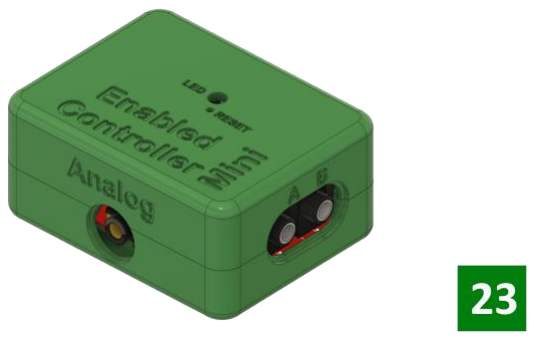
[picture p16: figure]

20

Step 22: Insert the top enclosure part over the bottom enclosure and snap them together.
Step 23 – That’s it! Your Enabled-Controller-Mini is fully assembled and ready to use.

ready to use.

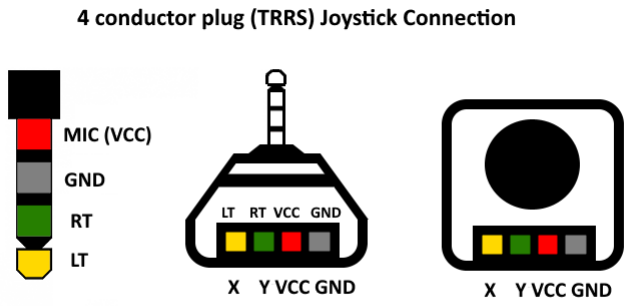
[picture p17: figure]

21

### Joystick Assembly

Enabled-Controller includes one 4 conductors input 3.5mm jack reserved to connect a dual axis joystick. The order of pins in joystick boards can vary depending on the brand but the following general configuration can be used to attach analog joystick. Enabled-Controller is designed to work with analog joystick which rated to work with 3.3V input voltage.

Figure 1: 4 Conductor plug (TRRS) pin mapping

The following table can summarize figure 1 as following:

PIN | FUNCTION
1 (Sleeve) | Microphone – VCC (3.3V)
2 (Ring 2) | GND
3 (Ring 1) | RT(Right Audio Channel)
4 (Tip) | LT(Left Audio Channel)
Table 1: 4 Conductor plug (TRRS) pin mapping

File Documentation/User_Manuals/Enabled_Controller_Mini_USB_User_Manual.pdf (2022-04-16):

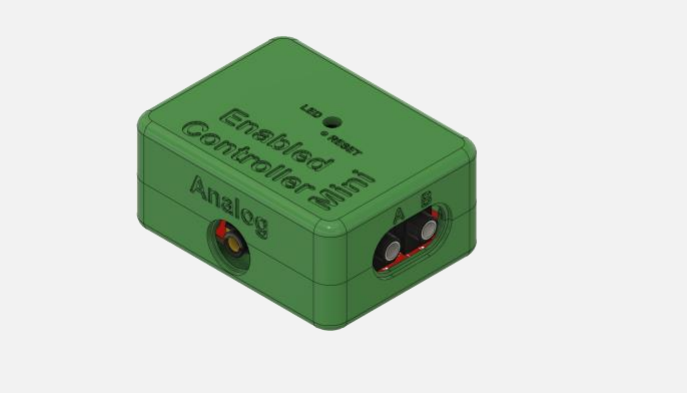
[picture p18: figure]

# ENABLED-CONTROLLER-MINI USB USER MANUAL

An accessible adaptive switch interface box

### Milad Hajihassan

https://github.com/milador/Enabled-Controller-Mini

1

## Contents

Usage | 2
Keyboard Switch mode | 2
Morse Keyboard Mode | 4
Morse Mouse Mode | 4
Settings Mode | 5
Customization | 6

2

## Usage

The Enabled-Controller-Mini USB can used in different configurations based on the needs of the end user. The Enabled-Controller-Mini hardware can be used along different software as input device for multiple devices. The hardware allows you connect up to four input 3.5mm adaptive switches which are marked A,B,C,D on both circuit board and the enclosure.

All four switches can be used as inputs when short pressed and switch D can be used to change the operation mode when it’s pressed and hold for more than 2 seconds. Table 1 represents all the possible actions for switches and their corresponding led feedback.

Button | Action | Color
A | Short press | Blue
B | Short press | Red
C | Short press | Green
D | Short press | Yellow
D | Long Press | Mode Led Color
Table 1: Enabled-Controller-Mini USB switch actions and feedback

The device will blink two times in the color of operating mode when the initialization process is completed and will stay in that color. The led will blink momentary in color of the switch pressed as represented in Table 1 and the led color will go back to the color of operating mode. The mode can only change when switch D is pressed and hold for 2 seconds.

The USB version is great for usage along computer or smartphone devices as it’s able to simulate a USB mouse or USB keyboard device. The USB version can operate in different modes as it’s represented in Table 2.

Mode Number | Mode | Color
1 | Keyboard Switch | Teal
2 | Morse Keyboard | Purple
3 | Morse Mouse | Pink
4 | Settings | Orange
Table 2: Enabled-Controller-Mini USB modes

Keyboard Switch mode
The Keyboard Switch will operate similar to a four key keyboard which is great for using as switches for your computer or smartphone device through features such as Switch access and it can also be used to play computer games via WASD format keyboard.

The switch mode does not work the exact same way in all the Operating Systems and as the results, you may need to modify the keystrokes sent for each switch.

Enabled-Controller has two OS profile options which you can select from depending on the Operating System of your host device.

3

OS PROFILE #1: Windows and Android

Button | Action | Color | Result
A | Short press | Blue | Send ‘a’ keystroke
B | Short press | Red | Send ‘b’ keystroke
C | Short press | Green | Send ‘c’ keystroke
D | Short press | Yellow | Send ‘d’ keystroke
D | Long Press | Mode Led Color | Change operating mode
Table 3: Enabled-Controller-Mini USB switch actions (OS PROFILE #1)

OS PROFILE #2: macOS

Button | Action | Color | Result
A | Short press | Blue | Send KEY_F1 keystroke
B | Short press | Red | Send KEY_F2 keystroke
C | Short press | Green | Send KEY_F3 keystroke
D | Short press | Yellow | Send KEY_F4 keystroke
D | Long Press | Mode Led Color | Change operating mode
Table 4: Enabled-Controller-Mini USB switch actions (OS PROFILE #2)

The time between each switch press actions is calculated by switch reaction levels which can be changed in settings mode or manually through the software. The switch reaction time variable is used to calculate the reaction time for each of the 10 levels as represented in Table 5.

SWITCH_REACTION_TIME 50

The switch reaction time variable is set to 50 by default.

Level | 10 | 9 | 8 | 7 | 6 | 5 | 4 | 3 | 2 | 1
Time (ms) | 1*50 | 2*50 | 3*50 | 4*50 | 5*50 | 6*50 | 7*50 | 8*50 | 9*50 | 10*50

Table 5: Enabled-Controller-Mini USB switch reaction time

4

Morse Keyboard Mode
This mode is used to convert morse code to keystrokes via 2 switches. The first switch acts as dot and second switch acts as dash as explained in Table 6.
Button | Action | Color | Result
A | Short press | Blue | Send ‘.’ To morse stack
B | Short press | Red | Send ‘-’ To morse stack
D | Long Press | Mode Led Color | Change operating mode
Table 6: Enabled-Controller-Mini USB morse keyboard mode

The conversion of morse code combination to characters is done in software based on the static variables in the beginning of the code. These values can be customized based on your needs.

MORSE_TIMEOUT 1000

MORSE_REACTION_TIME 10

The timeout is the time in ms that is measured since last switch action to perform the morse conversation and send the result as keystroke. The time by default is set to 1 second ( 1000 ms ) which means the device will convert the morse code combinations if switch A and B (Dot , Dash ) are not pressed for 1 second.

The reaction time is the multiplier for time between each dot and dash. The higher reaction level means lower reaction time. The reaction levels can be changed using switches in the settings mode but it’s also possible to change the morse reaction time multiplier in the code. Table 7 can be used to understand the morse reaction time calculation.

Lev el | 10 | 9 | 8 | 7 | 6 | 5 | 4 | 3 | 2 | 1
Time (ms) | (1.5^1)* 10 | (1.5^2)* 10 | (1.5^3)* 10 | (1.5^4)* 10 | (1.5^5)* 10 | (1.5^6)* 10 | (1.5^7)* 10 | (1.5^8)* 10 | (1.5^9)* 10 | (1.5^10)* 10

Table 7: Enabled-Controller-Mini USB morse reaction time

The table of morse code combinations can be found on EasyMorse (https://github.com/milador/EasyMorse) project github repository.

Morse Mouse Mode
This mode is used to convert morse code to mouse via 2 switches. The first switch acts as dot and second switch acts as dash as explained in Table 8.
Button | Action | Color | Result
A | Short press | Blue | Send ‘.’ To morse stack
B | Short press | Red | Send ‘-’ To morse stack
D | Long Press | Mode Led Color | Change operating mode
Table 8: Enabled-Controller-Mini USB morse mouse mode

This mode users the morse timeout value and morse reaction time to convert morse code combinations to mouse actions similar to morse keyboard mode. The table of morse code combinations can be found on EasyMorse (https://github.com/milador/EasyMorse) project github repository. The conversion table is represented in Table 9 in addition.

5

Morse code | Result
- Move Up
-- | Move Down
.. | Move Left
... | Move Right
.- | Left Click
.-- | Right Click
..- | Double Left Click
..-- | Double Right Click
-. | Left Click & Hold/Release
-.. | Right Click & Hold/Release
Table 9: Enabled-Controller-Mini USB morse mouse code conversion table

The mouse move actions are fixed in terms of number of pixels that cursor can be moved for each morse code combination , but there is mouse move multiplier variable available in the software that allows you to customize the mouse move behavior based on your needs.

MOUSE_MOVE_MULTI 2

The mouse move multiplier variable is set to 2 by default.

Settings Mode
The settings mode is used to change the reaction level and reaction time using the A and B switches. The led will blink in blue when react level is increased and in red when reaction level is decreased. The number of led blinks indicate new reaction level. The led will blink 10 times when it reaches maximum or minimum reaction levels.
Button | Action | Color | Result
A | Short press | Blue | Increase Reaction level (Decrease Reaction time)
B | Short press | Red | Decrease Reaction level (Increase Reaction time)
D | Long Press | Mode Led Color | Change operating mode
Table 10: Enabled-Controller-Mini USB settings mode

There are total of 10 levels and the switch reaction times and morse reaction times can be calculated using Tablets 11 and 12.

Level | 10 | 9 | 8 | 7 | 6 | 5 | 4 | 3 | 2 | 1
Time (ms) | 1*50 | 2*50 | 3*50 | 4*50 | 5*50 | 6*50 | 7*50 | 8*50 | 9*50 | 10*50

Table 11: Enabled-Controller-Mini USB switch reaction time

Lev el | 10 | 9 | 8 | 7 | 6 | 5 | 4 | 3 | 2 | 1
Time (ms) | (1.5^1)* 10 | (1.5^2)* 10 | (1.5^3)* 10 | (1.5^4)* 10 | (1.5^5)* 10 | (1.5^6)* 10 | (1.5^7)* 10 | (1.5^8)* 10 | (1.5^9)* 10 | (1.5^10)* 10

Table 12: Enabled-Controller-Mini USB morse reaction time

6

### Customization

The Enabled-Controller-Mini USB can easily be customized by changing the value of variables at the beginning of Enabled-Controller-Mini USB software. The following variables can be changed for customization purposes:

#define SWITCH_MAC_PROFILE false

This variable is created to set the keys to be used as switches based on host device OS profile (Windows & Android = false , macOS = true )

#define MORSE_TIMEOUT 1000

The time of no activity which is used as flag to convert the morse combination to keystroke

#define MORSE_REACTION_TIME 10

The morse reaction time multiplier between each dot and dash actions

#define MOUSE_MOVE_MULTI 2

The morse mouse move multiplier variable

#define SWITCH_REACTION_TIME 50

The switch reaction time multiplier between each switch action

#define SWITCH_MODE_CHANGE_TIME 2000

The time that switch D needs to be hold in ms to perform mode change action

#define LED_BRIGHTNESS 150

The brightness of led for mode indication

#define LED_ACTION_BRIGHTNESS 150

The brightness of led for action indication

//Switch properties

const switchStruct switchProperty[] {

{1,"DOT",'a',5,1}, | //{1=dot,"DOT",'a',5=blue,1=1xMORSE_REACTION}
{2,"DASH",'b',6,3}, | //{2=dash,"DASH",'b',6=red,3=3xMORSE_REACTION}
{3,"",'c',1,1}, | //{3,"",'c',1=green,1=1xMORSE_REACTION}
{4,"",'d',3,1} | //{4,"",'d',3=yellow,1=1xMORSE_REACTION}

};

The values of third column can be changed to different characters and the fourth column can be changed for customization of led feedback.

7

//Settings Action properties

const settingsActionStruct settingsProperty[] {

{1,"Increase Reaction",5}, | //{1=Increase Reaction,5=blue}
{2,"Decrease Reaction",6}, | //{2=Decrease Reaction,6=red}
{3,"Max Reaction",1}, | //{3=Max Reaction,1=green}
{4,"Min Reaction",1} | //{4=Min Reaction,1=green}

};

The third column can be changed for customization of led feedback.

//Mode properties

const modeStruct modeProperty[] {

{1,"Keyboard Switch",8},

{2,"Morse Keyboard",7},

{3,"Morse Mouse",2},

{4,"Settings",4}

};

The third column can be changed for customization of led feedback.

const colorStruct colorProperty[] {

{1,"Green",{0,50,0}},

{2,"Pink",{50,00,20}},

{3,"Yellow",{50,50,0}},

{4,"Orange",{50,20,0}},

{5,"Blue",{0,0,50}},

{6,"Red",{50,0,0}},

{7,"Purple",{50,0,50}},

{8,"Teal",{0,128,128}}

};

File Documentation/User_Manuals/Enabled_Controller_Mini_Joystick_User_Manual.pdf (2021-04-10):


# ENABLED-CONTROLLER-MINI JOYSTICK USER MANUAL

An accessible adaptive switch interface box

### Version 1.1

https://github.com/milador/Enabled-Controller-Mini

1

## Contents

Usage | 2
Customization | 2

2

## Usage

The Enabled Controller Mini Joystick can used in different configurations based on the needs of the end user. The Enabled Controller Mini hardware can be used along different software as input device for multiple devices. The hardware allows you connect up to eight input 3.5mm adaptive switches which are marked A,B,C,D,UP on both circuit board and the enclosure.

Four switches marked as A,B,C,D can be used as input buttons when short pressed.

Table 1 represents all the possible actions for switches and their corresponding led feedback.

Button | XAC | Action | Color
A | X1 | Short press | Blue
B | X2 | Short press | Yellow
C | A | Short press | Green
D | B | Short press | Red
Table 1: Enabled Controller Mini Joystick switch actions and feedback

The device will blink two times in the color of operating mode when the initialization process is completed and will stay in that color. The led will blink momentary in color of the switch pressed as represented in Table 1 and the led color will go back to the color of operating mode.

The Joystick version is great for usage along computer or for gaming purposes as it’s able to simulate an USB joystick device. The Joystick version can operate in different modes as it’s represented in Table 2.

Mode Number | Mode | Color
1 | Mode 1 | Teal
Table 2: Enabled Controller Mini Joystick modes

The Analog four connection input 3.5mm adaptive switches is used to connect a dual axis joystick (X axis and Y axis).

### Customization

The Enabled Controller Mini joystick can easily be customized by changing the value of variables at the beginning of Enabled Controller Mini Joystick software. The following variables can be changed for customization purposes:

#define JOYSTICK_DEADZONE 20

The deadzone value of analog joystick for each axis

#define SWITCH_REACTION_TIME 50

The switch reaction time multiplier between each switch action

#define SWITCH_MODE 1

There’s only one switch mode available

3

#define LED_BRIGHTNESS 100

The brightness of led for mode indication

#define LED_ACTION_BRIGHTNESS 100

The brightness of led for action indication

//Switch properties

const switchStruct switchProperty[] {

{1,"X1",1,5,5},

{2,"X2",2,6,3},

{3,"A",3,7,1},

{4,"B",4,8,6}

};

The third column can be changed for customization of led feedback.

//Mode properties

const modeStruct modeProperty[] {

{1,"Mode 1",8}

};

The third column can be changed for customization of led feedback.

const colorStruct colorProperty[] {

{1,"Green",{0,50,0}},

{2,"Pink",{50,00,20}},

{3,"Yellow",{50,50,0}},

{4,"Orange",{50,20,0}},

{5,"Blue",{0,0,50}},

{6,"Red",{50,0,0}},

{7,"Purple",{50,0,50}},

{8,"Teal",{0,128,128}}

};

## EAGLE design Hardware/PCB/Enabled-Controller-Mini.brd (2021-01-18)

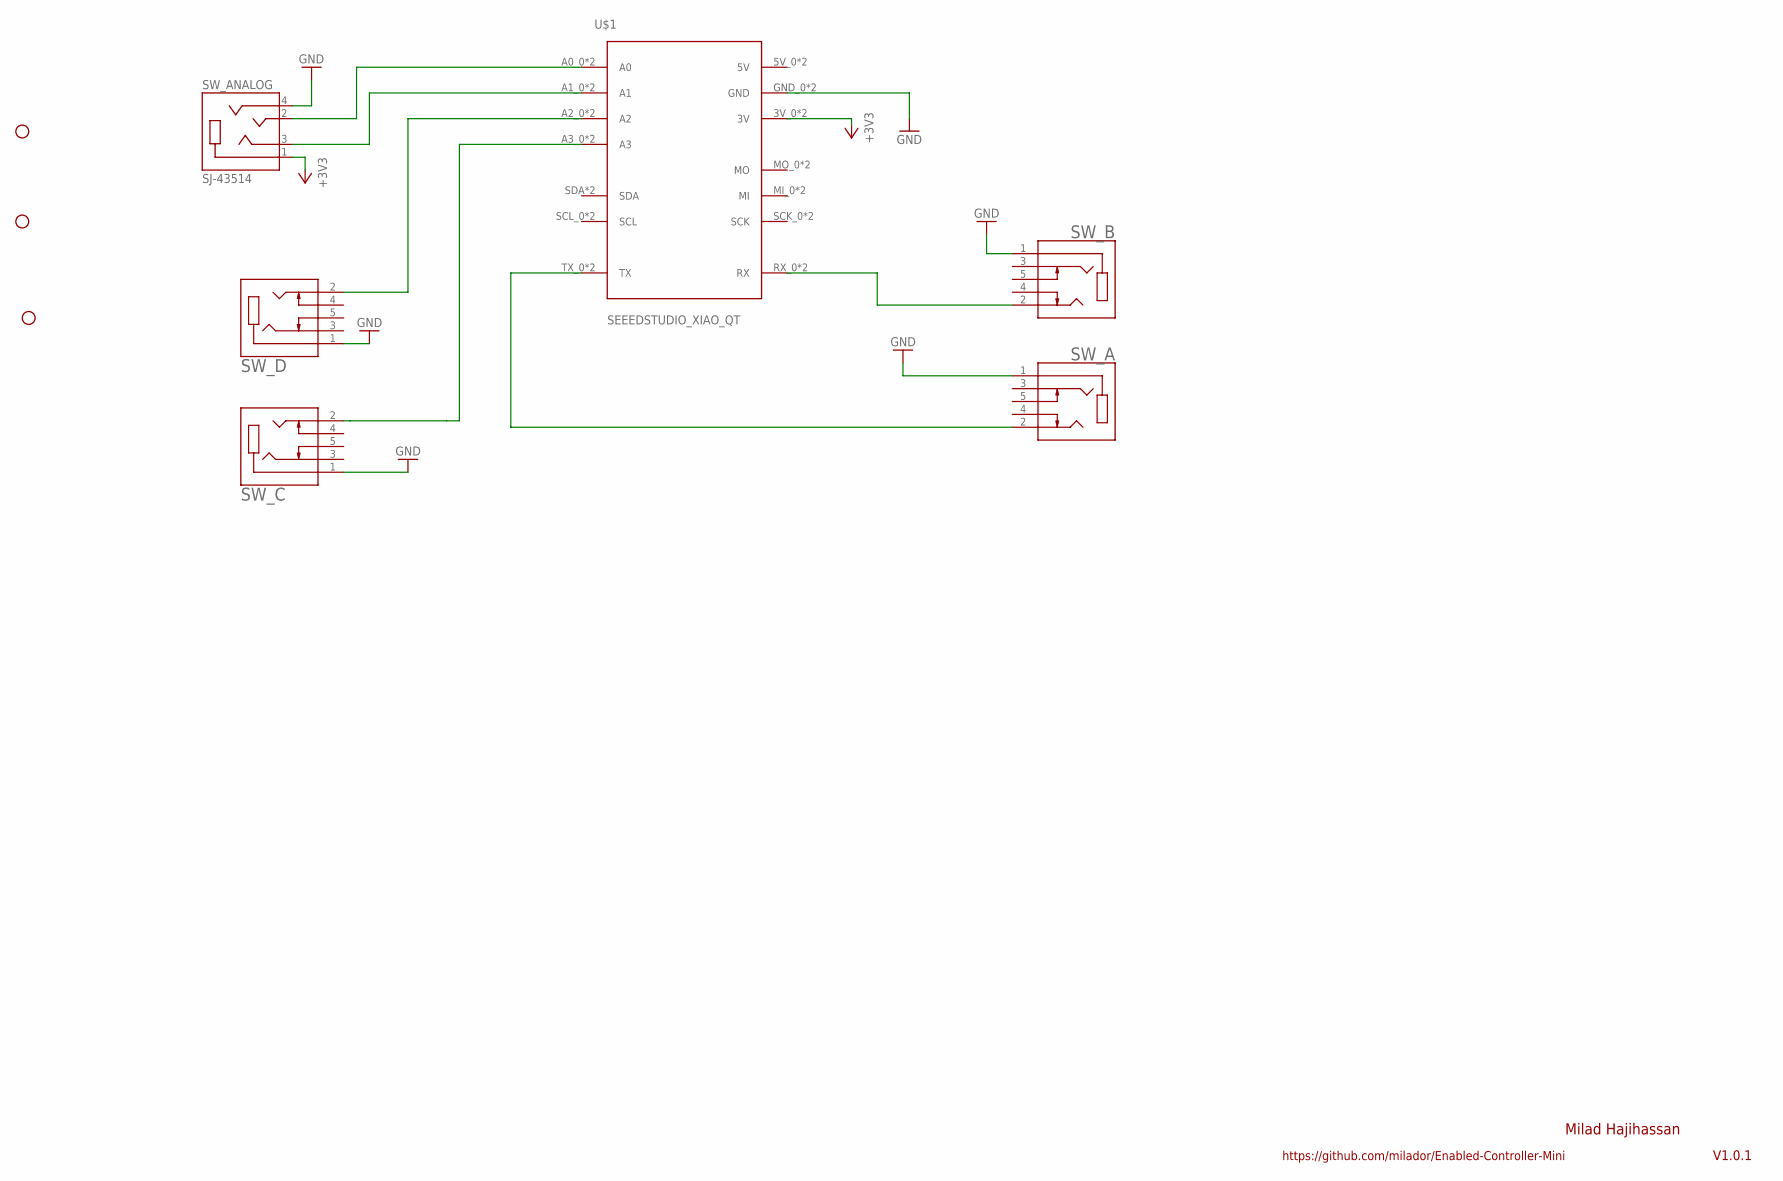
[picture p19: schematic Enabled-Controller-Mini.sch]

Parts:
STANDOFF1, STANDOFF2, STANDOFF3: STAND-OFF-; STAND-OFF
SW_A: CUI_SJ1-3535NGSJ1-3535NG; CUI_SJ1-3535NG
SW_ANALOG: SJ-43514; CUI_SJ-43514
SW_B: CUI_SJ1-3535NGSJ1-3535NG; CUI_SJ1-3535NG
SW_C: CUI_SJ1-3535NGSJ1-3535NG; CUI_SJ1-3535NG
SW_D: CUI_SJ1-3535NGSJ1-3535NG; CUI_SJ1-3535NG
U$1: SEEEDSTUDIO_XIAO_QT; SEEEDSTUDIO_XIAO

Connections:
+3V3: SW_ANALOG.1 (SLEEVE), U$1.3V_0 (3V), U$1.3V_1 (3V)
GND: SW_A.1, SW_ANALOG.4 (RING2), SW_B.1, SW_C.1, SW_D.1, U$1.GND_0 (GND), U$1.GND_1 (GND)
unnamed: SW_B.2, U$1.RX_0 (RX), U$1.RX_1 (RX)
unnamed: SW_A.2, U$1.TX_0 (TX), U$1.TX_1 (TX)
unnamed: SW_ANALOG.2 (TIP), U$1.A0_0 (A0), U$1.A0_1 (A0)
unnamed: SW_C.2, U$1.A3_0 (A3), U$1.A3_1 (A3)
unnamed: SW_ANALOG.3 (RING1), U$1.A1_0 (A1), U$1.A1_1 (A1)
unnamed: SW_D.2, U$1.A2_0 (A2), U$1.A2_1 (A2)

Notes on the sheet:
V1.0.1
Milad Hajihassan
https://github.com/milador/Enabled-Controller-Mini

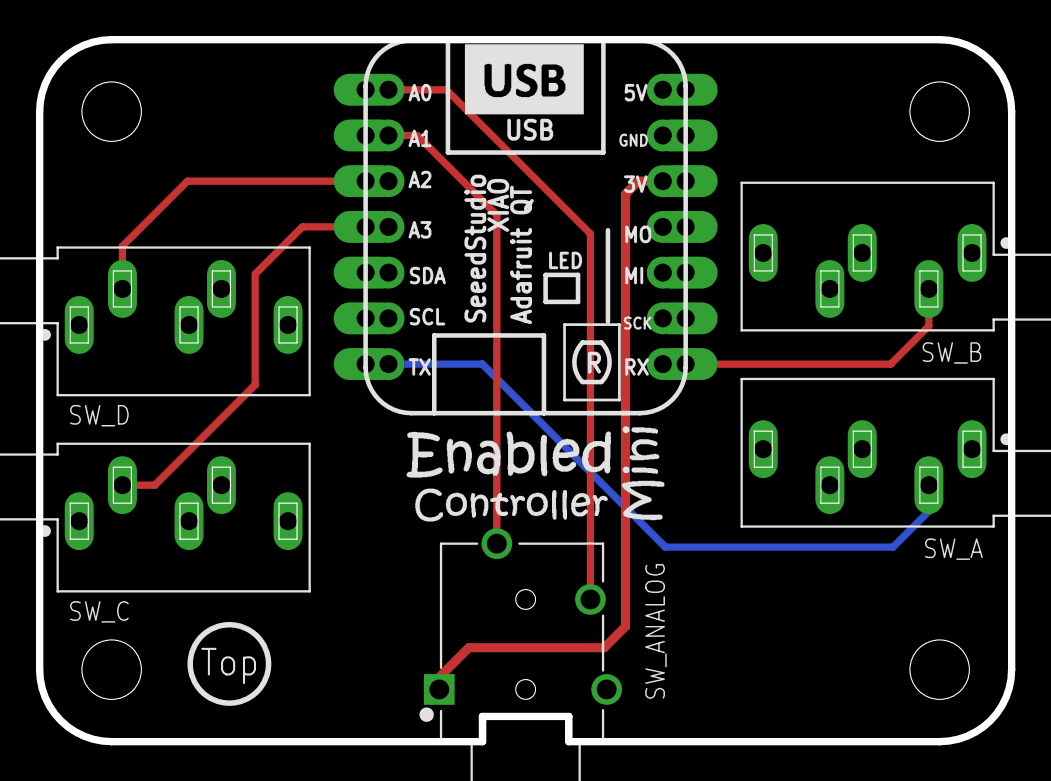
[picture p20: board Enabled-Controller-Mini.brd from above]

Board: 2 copper layers, 54.0 x 39.0 mm, 10 parts (0 on the bottom side), 8 nets.

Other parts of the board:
STANDOFF44: STAND-OFF-; STAND-OFF

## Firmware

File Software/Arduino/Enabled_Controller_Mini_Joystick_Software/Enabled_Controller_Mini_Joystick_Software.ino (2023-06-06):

/***************************************************************************
 * File Name: Enabled_Controller_Mini_Joystick_Software.ino 
 * Title: Enabled Controller Mini Joystick Software
 * Developed by: Milad Hajihassan
 * Version Number: 1.2 (01/6/2023)
 * Github Link: https://github.com/milador/Enabled_Controller_Mini
 ***************************************************************************/

#include "XACGamepad.h"
#include <math.h>
#include <Adafruit_NeoPixel.h>


//Can be changed based on the needs of the users 
#define JOYSTICK_DEADZONE 20                                          //Joystick deadzone
#define SWITCH_REACTION_TIME 50                                       //Minimum time for each switch action
#define SWITCH_MODE 1                                                 //Only one mode
#define JOYSTICK_ENABLED true                                          //Joystick enabled or diabled

#define LED_BRIGHTNESS 100                                             //The mode led color brightness which is always on ( Use a low value to decrease power usage )
#define LED_ACTION_BRIGHTNESS 100                                      //The action led color brightness which can be a higher value than LED_BRIGHTNESS


//Define Switch pins
#define LED_PIN 11


#define SWITCH_A_PIN 6
#define SWITCH_B_PIN 7
#define SWITCH_C_PIN 3
#define SWITCH_D_PIN 2

//Define Joystick pins
#define JOYSTICK_X1_PIN A0
#define JOYSTICK_Y1_PIN A1  


// Variable Declaration

//Declare switch state variables for each switch
int switchAState;
int switchBState;
int switchCState;
int switchDState;

//Previous status of switches
int switchAPrevState = HIGH;          
int switchBPrevState = HIGH;
int switchCPrevState = HIGH;
int switchDPrevState = HIGH;

//Declare joystick variables 
int joystickX;
int joystickY;


//Declare Switch variables for settings 
int switchConfigured;
int switchReactionTime;
int switchReactionLevel;
int switchMode;


//RGB LED Color code structure 

struct rgbColorCode {
    int r;    // red value 0 to 255
    int g;   // green value
    int b;   // blue value
 };

//Color structure 
typedef struct { 
  uint8_t colorNumber;
  String colorName;
  rgbColorCode colorCode;
} colorStruct;

 //Mode structure 
typedef struct { 
  uint8_t modeNumber;
  String modeName;
  uint8_t modeColorNumber;
} modeStruct;


 //Switch structure 
typedef struct { 
  uint8_t switchNumber;
  String switchButtonName;
  uint8_t switchModeButtonNumber;
  uint8_t switchColorNumber;
} switchStruct;


 //Settings Action structure 
typedef struct { 
  uint8_t settingsActionNumber;
  String settingsActionName;
  uint8_t settingsActionColorNumber;
} settingsActionStruct;

//Color properties 
const colorStruct colorProperty[] {
    {1,"Green",{60,0,0}},
    {2,"Pink",{0,50,60}},
    {3,"Yellow",{60,50,0}},    
    {4,"Orange",{20,60,0}},
    {5,"Blue",{0,0,60}},
    {6,"Red",{0,60,0}},
    {7,"Purple",{0,50,128}},
    {8,"Teal",{128,0,128}}       
};

//Switch properties 
const switchStruct switchProperty[] {
    {1,"A",1,5},
    {2,"B",2,3},
    {3,"C",3,1},
    {4,"D",4,6}
};

//Mode properties 
const modeStruct modeProperty[] {
    {1,"Mode 1",8}
};


//Setup NeoPixel LED
Adafruit_NeoPixel ledPixels = Adafruit_NeoPixel(1, LED_PIN, NEO_GRB + NEO_KHZ800);

//Starts an instance of the XAC compatible gamepad object
XACGamepad gamepad;
 

void setup() {
  
  gamepad.begin();
  ledPixels.begin();                                                           //Start NeoPixel
  Serial.begin(115200);                                                        //Start Serial
  switchSetup();
  delay(1000);
  initLedFeedback();                                                          //Led will blink in a color to show the current mode 
  delay(5);
  displayFeatureList();
  
  //Initialize the switch pins as inputs
  pinMode(SWITCH_A_PIN, INPUT_PULLUP);    
  pinMode(SWITCH_B_PIN, INPUT_PULLUP);   
  pinMode(SWITCH_C_PIN, INPUT_PULLUP);    
  pinMode(SWITCH_D_PIN, INPUT_PULLUP);  

  //Initialize the LED pin as an output
  pinMode(LED_PIN, OUTPUT);                                                


};

void loop() {
  //Perform joystick actions based on the mode
  joystickAction(switchMode);
  ledPixels.show(); 
  delay(5);
}

//***DISPLAY FEATURE LIST FUNCTION***//

void displayFeatureList(void) {

  Serial.println(" ");
  Serial.println(" --- ");
  Serial.println("This is the Enabled Controller Mini XAC Compatible Gamepad Software");
  Serial.println(" ");
  Serial.println("VERSION: 1.2 (1 June 2023)");
  Serial.println(" ");
  Serial.println(" --- ");
  Serial.println("Features: XAC Compatible Gamepad");
  Serial.println(" --- ");
  Serial.println(" ");

}

//***RGB LED FUNCTION***//

void setLedBlink(int numBlinks, int delayBlinks, int ledColor,uint8_t ledBrightness) {
  if (numBlinks < 0) numBlinks *= -1;

      for (int i = 0; i < numBlinks; i++) {
        ledPixels.setPixelColor(0, ledPixels.Color(colorProperty[ledColor-1].colorCode.g,colorProperty[ledColor-1].colorCode.r,colorProperty[ledColor-1].colorCode.b));
        ledPixels.setBrightness(ledBrightness);
        ledPixels.show(); 
        delay(delayBlinks);
        ledPixels.setBrightness(ledBrightness);
        ledPixels.setPixelColor(0, ledPixels.Color(0,0,0));
        ledPixels.setBrightness(ledBrightness);
        ledPixels.show(); 
        delay(delayBlinks);
      }
}

//***UPDATE RGB LED COLOR FUNCTION***//

void updateLedColor(int ledColor, uint8_t ledBrightness) {
    ledPixels.setPixelColor(0, ledPixels.Color(colorProperty[ledColor-1].colorCode.g,colorProperty[ledColor-1].colorCode.r,colorProperty[ledColor-1].colorCode.b));
    ledPixels.setBrightness(ledBrightness);
    ledPixels.show();
}

//***GET RGB LED COLOR FUNCTION***//

uint32_t getLedColor(int ledModeNumber) {

  int colorNumber= modeProperty[ledModeNumber-1].modeColorNumber-1;
  
  return (ledPixels.Color(colorProperty[colorNumber].colorCode.g,colorProperty[colorNumber].colorCode.r,colorProperty[colorNumber].colorCode.b));
}

//***GET RGB LED BRIGHTNESS FUNCTION***//

uint8_t getLedBrightness() {
  return (ledPixels.getBrightness());
}

//***SET RGB LED COLOR FUNCTION***//

void setLedColor (uint32_t ledColor, uint8_t ledBrightness){
    
  ledPixels.setPixelColor(0, ledColor);
  ledPixels.setBrightness(ledBrightness);
  ledPixels.show(); 

}

//***SET RGB LED BRIGHTNESS FUNCTION***//

void setLedBrightness(uint8_t ledBrightness) {
  ledPixels.setBrightness(ledBrightness);
  ledPixels.show();
}

//***CLEAR RGB LED FUNCTION***//

void ledClear() {
  ledPixels.setPixelColor(0, ledPixels.Color(0,0,0));
  ledPixels.show(); 
}

//***SWITCH FEEDBACK FUNCTION***//

void switchFeedback(int switchNumber,int modeNumber,int delayTime, int blinkNumber =1)
{
  //Get previous led color and brightness 
  uint32_t previousColor = getLedColor(modeNumber);
  uint8_t previousBrightness = getLedBrightness();
 
  setLedBlink(blinkNumber,delayTime,switchProperty[switchNumber-1].switchColorNumber,LED_ACTION_BRIGHTNESS);
  delay(5);

  //Set previous led color and brightness 
  setLedColor(previousColor,previousBrightness);
  
}

//***MODE FEEDBACK FUNCTION***//

void modeFeedback(int modeNumber,int delayTime, int blinkNumber =1)
{

   //Get new led color and brightness 
  uint32_t newColor = getLedColor(modeNumber);
  uint8_t newBrightness = getLedBrightness();
  
  setLedBlink(blinkNumber,delayTime,modeProperty[modeNumber-1].modeColorNumber,LED_ACTION_BRIGHTNESS);
  delay(5);

  //Set new led color and brightness 
  setLedColor(newColor,newBrightness);
  
}

//***PERFORM JOYSTICK ACTIONS FUNCTION***//

void joystickAction(int mode) {

    //Update status of switch inputs
  switchAState = digitalRead(SWITCH_A_PIN);
  switchBState = digitalRead(SWITCH_B_PIN);
  switchCState = digitalRead(SWITCH_C_PIN);
  switchDState = digitalRead(SWITCH_D_PIN);

  

  //Update joystick values based on available joystick number 
  if(JOYSTICK_ENABLED) {
    joystickX = analogRead(JOYSTICK_X1_PIN);
    joystickY = analogRead(JOYSTICK_Y1_PIN);

    //Perform joystick move Actions
    int xx = map(joystickX, 0, 1023, -127, 127);
    int yy = map(joystickY, 0, 1023, -127, 127);
    

    if (xx<=JOYSTICK_DEADZONE && xx>=-JOYSTICK_DEADZONE){
      gamepad.xAxis(0);  
      gamepad.send();
    }
    else {
      gamepad.xAxis(xx);  
      gamepad.send();  
    }

    if (yy<=JOYSTICK_DEADZONE && yy>=-JOYSTICK_DEADZONE){
      gamepad.yAxis(0);  
      gamepad.send();    
      }
    else {
      gamepad.yAxis(yy);  
      gamepad.send();    
    }
    
  } else {
    joystickX = 0;
    joystickY = 0;
  }


    //Perform button actions
    if(!switchAState) {
      switchFeedback(1,mode,switchReactionTime,1);
      gamepad.press(switchProperty[0].switchModeButtonNumber-1);
      gamepad.send();
    } else if(switchAState && switchAPrevState) {
      gamepad.release(switchProperty[0].switchModeButtonNumber-1);
      gamepad.send();
    }
    
    if(!switchBState) {
      switchFeedback(2,mode,switchReactionTime,1);
      gamepad.press(switchProperty[1].switchModeButtonNumber-1);
      gamepad.send();
    } else if(switchBState && switchBPrevState) {
      gamepad.release(switchProperty[1].switchModeButtonNumber-1);
      gamepad.send();
    }
    
    if(!switchCState) {
      switchFeedback(3,mode,switchReactionTime,1);
      gamepad.press(switchProperty[2].switchModeButtonNumber-1);
      gamepad.send();
    } else if(switchCState && switchDPrevState) {
      gamepad.release(switchProperty[2].switchModeButtonNumber-1);
      gamepad.send();
    }
    
    if(!switchDState) {
      switchFeedback(4,mode,switchReactionTime,1);
      gamepad.press(switchProperty[3].switchModeButtonNumber-1);
      gamepad.send();
    } else if(switchDState && switchDPrevState) {
      gamepad.release(switchProperty[3].switchModeButtonNumber-1);
      gamepad.send();
    }

    //Update previous state of buttons 
    switchAPrevState = switchAState;
    switchBPrevState = switchBState;
    switchCPrevState = switchCState;
    switchDPrevState = switchDState;
    
    delay(100);

}


//***SETUP SWITCH MODE FUNCTION***//

void switchSetup() {

    switchMode=SWITCH_MODE;
    switchReactionTime = SWITCH_REACTION_TIME;

    //Serial print settings 
    Serial.print("Switch Mode: ");
    Serial.println(switchMode);


    Serial.print("Reaction Time(ms): ");
    Serial.println(switchReactionTime);
}

//***INIT LED FEEDBACK FUNCTION***//

void initLedFeedback(){
  setLedBlink(2,500,modeProperty[switchMode-1].modeColorNumber,LED_ACTION_BRIGHTNESS);
  delay(5);
  updateLedColor(modeProperty[switchMode-1].modeColorNumber,LED_BRIGHTNESS);
  delay(5);
}

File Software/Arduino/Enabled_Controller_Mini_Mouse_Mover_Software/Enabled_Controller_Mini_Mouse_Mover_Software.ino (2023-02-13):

/** ************************************************************************
 * File Name: Enabled_Controller_Mini_Mouse_Mover_Software.ino 
 * Title: Enabled Controller Mini Mouse Mover Software
 * Developed by: Milad Hajihassan
 * Version Number: 1.0 (10/1/2023)
 * Github Link: https://github.com/milador/Enabled_Controller_Mini
 ***************************************************************************/

#include "Mouse.h"
#include <StopWatch.h>
#include <math.h>
#include <Adafruit_NeoPixel.h>
#include <FlashStorage.h>


//Can be changed based on the needs of the users
#define MOUSE_MOVER_XY 15                                             //Morse mouse move 
#define SWITCH_REACTION_TIME 50                                       //Minimum time for each switch action ( level 10 : 1x50 =50ms , level 1 : 10x50=500ms )
#define SWITCH_MODE_CHANGE_TIME 2000                                  //How long to hold switch 4 to change mode 

#define LED_BRIGHTNESS 150                                             //The mode led color brightness which is always on ( Use a low value to decrease power usage )
#define LED_ACTION_BRIGHTNESS 150                                      //The action led color brightness which can be a higher value than LED_BRIGHTNESS

//Define Mouse Actions
#define MOUSE_NO_ACTION 0 
#define MOUSE_MOVER_X 1
#define MOUSE_MOVER_Y 2
#define MOUSE_MOVER_CLICK 3

//Define Switch pins
#define LED_PIN 11

#define SWITCH_A_PIN 6
#define SWITCH_B_PIN 7
#define SWITCH_C_PIN 3
#define SWITCH_D_PIN 2

// Variable Declaration

//Declare switch state variables for each switch
bool switchAState;
bool switchBState;
bool switchCState;
bool switchDState;

bool previousSwitchAState = HIGH;
bool previousSwitchBState = HIGH;
bool previousSwitchCState = HIGH;
bool previousSwitchDState = HIGH;

/*
bool moverYState = true;                 // false = down , true = up 
bool moverXState = true;                 // false = left , true = right
bool moverClickState = true;             // false = left click , true = left click
*/
bool moverState[5] = {true,true,true,true};

//Stopwatches array used to time switch presses
StopWatch timeWatcher[3];
StopWatch switchDTimeWatcher[1];



//Declare Switch variables for settings 
int switchConfigured;
int switchReactionTime;
int switchReactionLevel;
int switchMode;

int morseReactionTime;

FlashStorage(switchConfiguredFlash, int);
FlashStorage(switchReactionLevelFlash, int);
FlashStorage(switchModeFlash, int);


//RGB LED Color code structure 

struct rgbColorCode {
    int r;    // red value 0 to 255
    int g;   // green value
    int b;   // blue value
 };

//Color structure 
typedef struct { 
  uint8_t colorNumber;
  String colorName;
  rgbColorCode colorCode;
} colorStruct;

 //Mode structure 
typedef struct { 
  uint8_t modeNumber;
  String modeName;
  uint8_t modeColorNumber;
} modeStruct;


 //Switch structure 
typedef struct { 
  uint8_t switchNumber;
  String switchName;
  uint8_t switchMouse;
  uint8_t switchColorNumber;
} switchStruct;


 //Settings Action structure 
typedef struct { 
  uint8_t settingsActionNumber;
  String settingsActionName;
  uint8_t settingsActionColorNumber;
} settingsActionStruct;

//Color properties 
const colorStruct colorProperty[] {
    {1,"Green",{60,0,0}},
    {2,"Pink",{0,50,60}},
    {3,"Yellow",{60,50,0}},    
    {4,"Orange",{20,60,0}},
    {5,"Blue",{0,0,60}},
    {6,"Red",{0,60,0}},
    {7,"Purple",{0,50,128}},
    {8,"Teal",{128,0,128}}       
};

const switchStruct switchProperty[] {
    {1,"Move-Y",MOUSE_MOVER_Y,5},                             
    {2,"Move-X",MOUSE_MOVER_X,6},                           
    {3,"Click",MOUSE_MOVER_CLICK,1},                             
    {4,"",MOUSE_NO_ACTION,3}         
};


//Settings Action properties 
const settingsActionStruct settingsProperty[] {
    {1,"Increase Reaction",5},                             //{1=Increase Reaction,5=blue}
    {2,"Decrease Reaction",6},                             //{2=Decrease Reaction,6=red}
    {3,"Max Reaction",1},                                  //{3=Max Reaction,1=green}
    {4,"Min Reaction",1}                                   //{4=Min Reaction,1=green}
};

//Mode properties 
const modeStruct modeProperty[] {
    {1,"Mouse Mover",8},
    {2,"Settings",4}
};
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

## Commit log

2021-01-17 Updated Enclosure : Snap wall height was increased by 0.8mm.
    [Enabled_Controller_Mini_Bottom.step, Enabled_Controller_Mini_Bottom.stl, Enabled_Controller_Mini_Bottom_With_Mount.step, Enabled_Controller_Mini_Bottom_With_Mo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]
2021-01-18 Added BOM file
    [Enabled_Controller_Mini_BOM.csv, Enabled_Controller_Mini_BOM.xlsx]
2021-01-18 Added Assembly Instructions Manual
2021-01-18 Added PCB Eagle design files and gerber files
    [Enabled-Controller-Mini.brd, Enabled-Controller-Mini.sch]
2021-01-21 Updated PCB design files : SWITCH GPIO's changed to A0,A1,A2,A3
    [Enabled-Controller-Mini.brd, Enabled-Controller-Mini.sch]
2021-01-21 Updated Gerber files : Version 1.1
    [Enabled-Controller-Mini.GBL, Enabled-Controller-Mini.GBO, Enabled-Controller-Mini.GBP, Enabled-Controller-Mini.GBS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]
2021-01-23 Reversed PCB design file
    [Enabled-Controller-Mini.brd, Enabled-Controller-Mini.sch]
2021-01-23 Updated STEP files
    [Enabled_Controller_Mini_Bottom.step, Enabled_Controller_Mini_Bottom_With_Mount.step, Enabled_Controller_Mini_Top.step]
2021-01-31 Updated Assembly manual 1.11
2021-01-31 Tested Arduino code: Basis functionality
2021-02-01 Added CircuitPython software setup
2021-08-21 Updated the top enclosure
    [Enabled_Controller_Mini_Top.step, Enabled_Controller_Mini_Top.stl]
2021-11-03 Added CircuitPython uf2 files
2021-11-03 Updated CircuitPython readme
2023-06-29 Update Version 1.3
    Updated Enclosure and assembly guide
    [Enabled_Controller_Mini_Bottom.step, Enabled_Controller_Mini_Bottom.stl, Enabled_Controller_Mini_Bottom_With_Mount.step, Enabled_Controller_Mini_Bottom_With_Mo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]

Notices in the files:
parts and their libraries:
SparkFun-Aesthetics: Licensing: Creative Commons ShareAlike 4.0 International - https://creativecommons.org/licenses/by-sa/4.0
